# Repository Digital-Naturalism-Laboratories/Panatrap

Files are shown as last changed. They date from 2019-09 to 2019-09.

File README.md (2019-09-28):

# Panatrap
This is an open-source collection of design files and code for turning commercially available 360 "VR" cameras into panoramic camera traps for studying wildlife in natural environments.
These are created in Gamboa, Panama, at Digital Naturalism Laboratories by Andrew Quitmeyer and Danielle Hoogendijk. Work on this project has been supported by:
- The Digital Naturalism Conference (www.dinacon.org)
- Conservation X Labs

## Cameras
The collection currently consists of 2 camera trap setups based on the

- Xiaomi Misphere (MADV in the USA)
 - Full electronic functional control over 
  - Turning camera ON/OFF
  - Switching camera from Video to Photo Mode
  - Trigger a photo or video recording

- Ricoh Theta V
 - Full electronic functional control over
  - Turning the camera on (waking from sleep mode)
  - Triggering a photo or video to begin recording

as we hack more cameras we will add them and their files to this list and repository.
We hacked the Ricoh Theta S and posted detailed instructions here:
but this was quite a destructive hack (we literally ripped the camera apart and soldered things to its button). The Panatrap project focuses on non-destructive, reversible hacks to turn your 360 camera into a cool trap

## Key Challenges
Loosely defined, camera traps are simply photographic instruments that can be remotely triggered by wildlife. Typically this is done with a PIR motion sensor triggering a camera to snap a photo.
Thus when transforming commercially available cameras to become camera traps, the key abilities we need are:
- Remote Triggering
 - The ability to tell the camera to snap a photo or start recording a video
- Low power consumption
 - Typically this is the ability to remotely turn the camera ON/OFF, or at least bring the camera in and out of a low power "sleep mode", and to remotely charge it
- Speedy Capture
 - We were told that a typical camera trap aims to go from sensing an animal's presence to capturing the creature in under 1/2 second
 - This ability is often at odds with the "Low power consumption" goal, since many cameras have a not-insignificant amount of wake up time when starting.
- Image quality
 - An ideal camera trap will provide a high resolution image of the captured animal
- Outdoor Readiness
 - The camera trap needs to be able to withstand being left alone for several days or weeks in its target environment.
 - Camera Traps face challenges from the elements (such as rain, heat, wind, and cold)
 - They also face challenges from local creatures (such as small insect destruction, or elephant smashing)

## Xiaomi Misphere
The first camera that we hacked because it has decent image quality, and importantly it has two exposed electrodes on the camera that make hacking very easy!

They made an interface on the bottom of the camera for the camera to be easily controlled with their included "selfie stick." It's just two metal electrodes that when connected it sends a message to the camera(the original selfie stick has a 220 ohm resistor connected to a button).
From our examinations, the 3 messages you can send to the camera with this interface are:
- Long Press (5 seconds)
 - Camera ON/OFF
- Medium Press (2 seconds)
 - Toggle Recording Mode (Video to Photo, or Photo to Video)
- Short press (0.5-1 seconds)
 - Shutter Button (Take a photo, or start or stop a video)
 
 ### Code
 Code is available in this repo
 
 ### Hardware
 Physical Designs are available here for free download:
 https://a360.co/2nrPLd8
 
 and included in this repo

## Ricoh Theta V
This camera was substantially more locked up  in our attempts to remotely operate it (especially in a way that allows for long term use and have a decently quick trigger).

The camera runs android, and has an acessible USB Api (to recieve PTP commands) and in theory has all the abilities to remotely A) Turn ON/OFF and B)Trigger a Photo Capture. But the firmware blocks some of these features (even if you switch into developer mode).

Luckily we discovered that sending an emulated Keyboard command (through something like a Teensy Arduino 3.2), can remotely wake up the camera (even though this feature is not documented anywhere!), and then we just need to trigger the photo.
The photo triggering is then done by a small servo connected to the arduino which manually taps the shutter button of the camera. The servo is shut down in between photos to reduce power consumption.

 ### Code
 Code is available in this repo
 
 ### Hardware
 Physical Designs are available here for free download:
 https://a360.co/2m22suQ
 and included in this repo

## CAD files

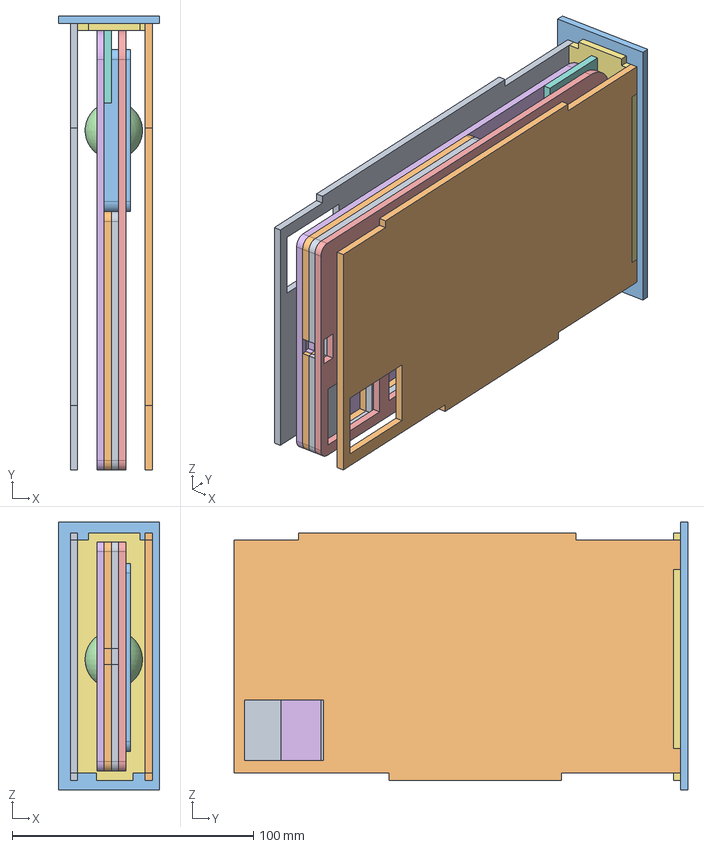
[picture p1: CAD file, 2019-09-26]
MADV/Designs/MADV-weather proof.stp
42.0 x 188.0 x 111.0 mm
holster
MADV body
Top Holder
Back Holder
Weather Sheild

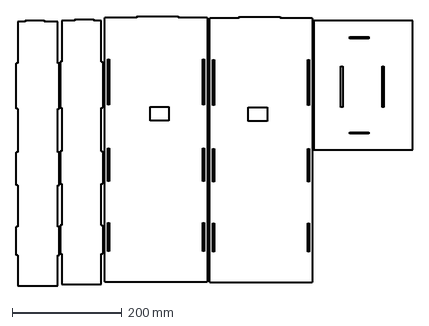
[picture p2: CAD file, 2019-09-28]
Theta_V/Designs/Weather ShieldTheta Servo Trigger Drawing v4 Sheet1.dxf
721.4 x 490.3 mm

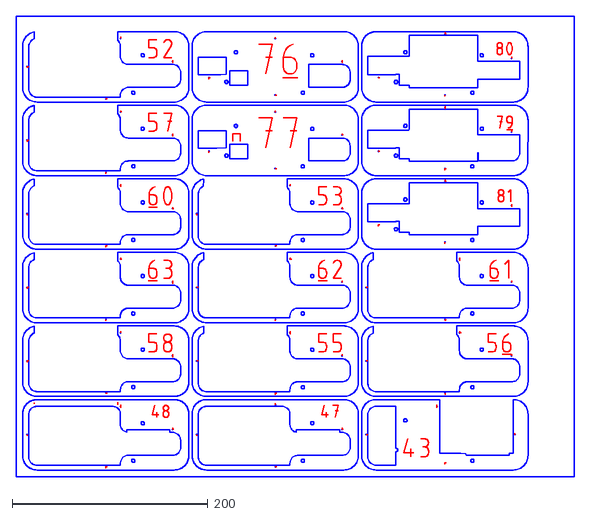
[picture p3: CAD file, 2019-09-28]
Theta_V/Designs/panatrap dxf-0.dxf
570.0 x 470.0

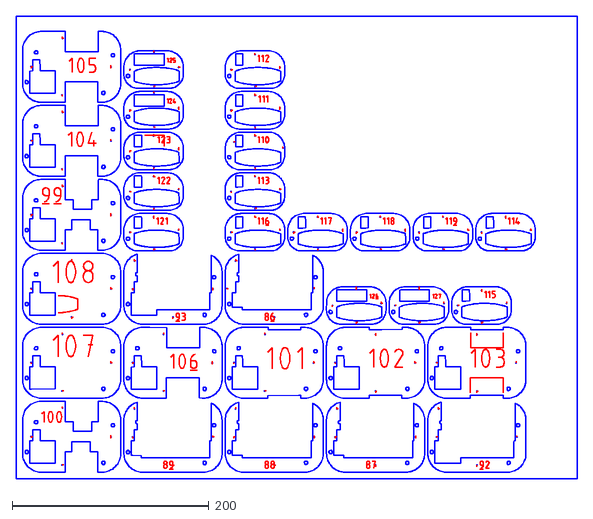
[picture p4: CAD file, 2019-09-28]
Theta_V/Designs/panatrap dxf-5.dxf
570.0 x 470.0

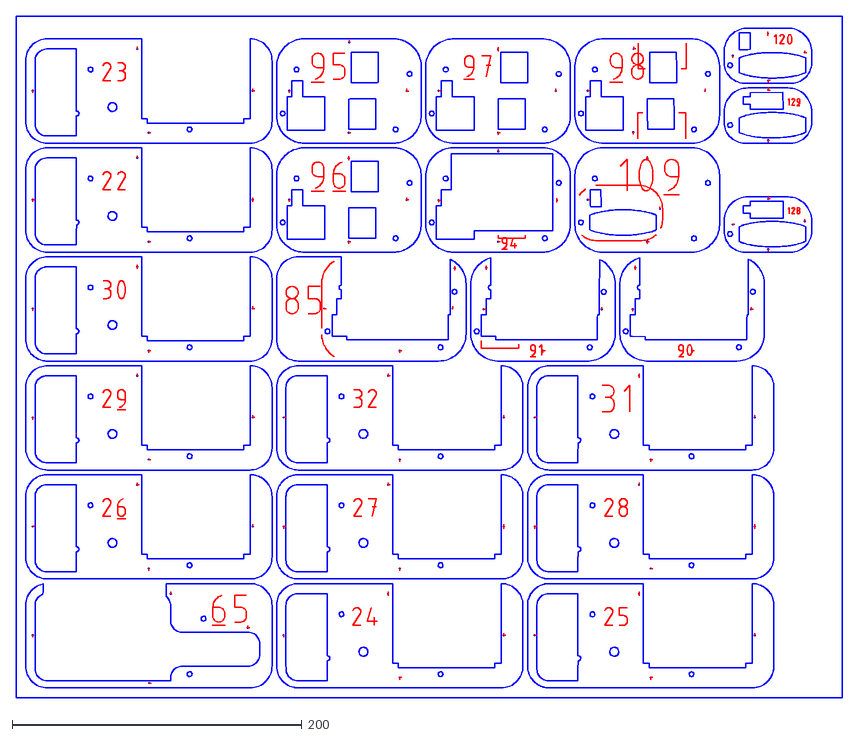
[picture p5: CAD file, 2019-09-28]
Theta_V/Designs/panatrap dxf-4.dxf
570.0 x 470.0

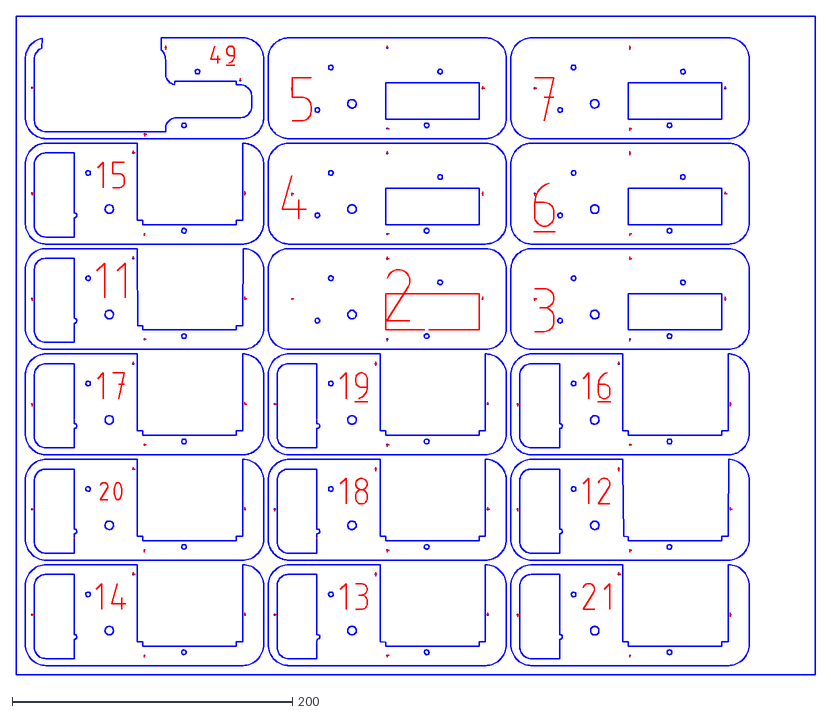
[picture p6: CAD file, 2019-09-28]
Theta_V/Designs/panatrap dxf-2.dxf
570.0 x 470.0

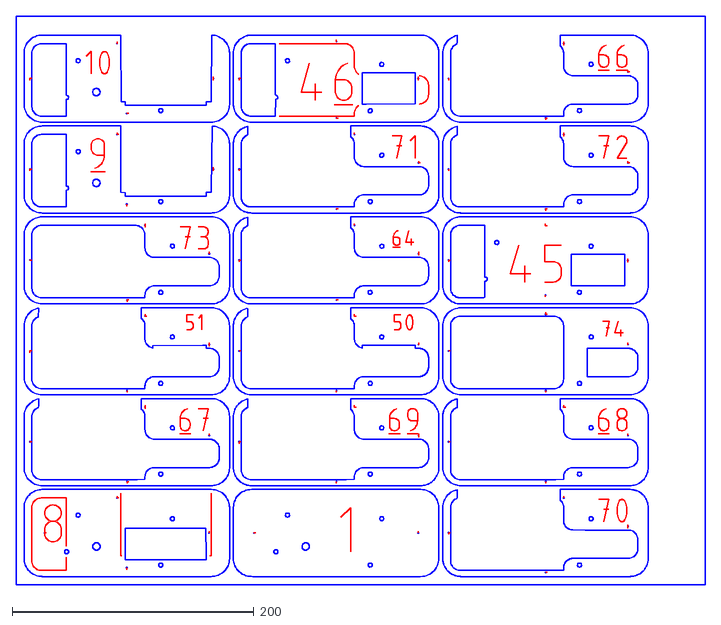
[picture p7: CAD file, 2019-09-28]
Theta_V/Designs/panatrap dxf-3.dxf
570.0 x 470.0

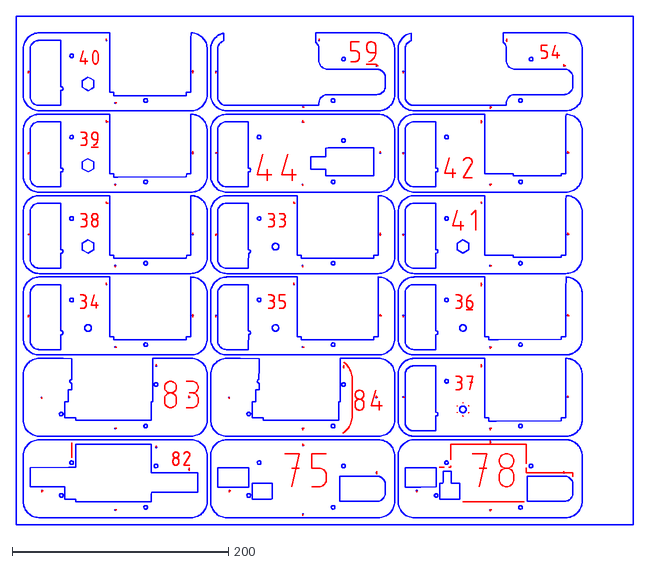
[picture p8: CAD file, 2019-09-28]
Theta_V/Designs/panatrap dxf-1.dxf
570.0 x 470.0

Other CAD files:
MADV/Designs/MADV-weather proof.f3d
MADV/Designs/MADV-weather proof.stl

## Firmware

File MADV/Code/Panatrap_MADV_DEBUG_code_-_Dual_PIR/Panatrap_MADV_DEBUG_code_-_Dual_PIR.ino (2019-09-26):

/*
  PanaTrap - MADV
  Debug Code for the turning the Xiaomi MiSphere (MADV) camera
  into a remotely controlled,
  PIR triggered, Camera Trap

*/

/* in order to trigger the MADV camera to change modes, in theory you should connect a relay to your arduino, and trigger that to connect the nodes of the MADV
  //But we are trying to use minimal hardware, and found that if you connect the node closest to the center of the camera to the ground, and then
  //Connect another digital pin  to the other node
  //Initially set the digital pin to HIGH, and then when you pull it LOW
  //it will trigger the camera

  - Long Press (5 seconds)
  - Camera ON/OFF
  - Medium Press (2 seconds)
  - Toggle Recording Mode (Video to Photo, or Photo to Video)
  - Short press (0.5-1 seconds)
  - Shutter Button (Take a photo, or start or stop a video)

*/

//Front PIR motion sensors
int fPIR = A4;
int fPIRval = -1;

//Back PIR motion sensors
int bPIR = A3;
int bPIRval = -1;

//camera trigger operants

int trigger = 12;
int gndtrigger = 9;


//LED for debugging display
int led = 13;


void setup() {
  //Serial for debugging PIRs
  // initialize serial communication at 9600 bits per second:
  Serial.begin(9600);

  //Turning some of the pins on the camera into virtual Power sources and Grounds
  pinMode(A1, OUTPUT);
  digitalWrite(A1, LOW);

  pinMode(A2, OUTPUT);
  digitalWrite(A2, HIGH);

  pinMode(A5, OUTPUT);
  digitalWrite(A5, LOW);


  //Camera Trigger stuff
  pinMode(led, OUTPUT);
  pinMode(trigger, OUTPUT);
  pinMode(gndtrigger, OUTPUT);

  digitalWrite(led, HIGH);

  digitalWrite(trigger, HIGH);
  digitalWrite(gndtrigger, LOW); //**Andy note A

}

// the loop routine runs over and over again forever:
void loop() {
  // read the input on analog pin 0:
  fPIRval = analogRead(fPIR);
  bPIRval = analogRead(bPIR);
  // print out the value you read:
  Serial.print(fPIRval);
  Serial.print("    rear:  ");
  Serial.println(bPIRval);


  if (fPIRval > 600 || bPIRval > 600) {
    critterDetected();
  }
  delay(1);        // delay in between reads for stability
}

void critterDetected() {

  Serial.println("Critter detected");
  //Turn camera on
  onOffCamera();

  //Take a photo
  takePhoto();
  takePhoto();

  //TODO: Wait to see if other critters still around
  //before we shut off camera

  //TODO: the camera will toggle between photo and video each time it shuts off, add in a toggle here

  onOffCamera();

}

void onOffCamera() {
  Serial.println("cameraONOFF");

  //5 second turn on
  digitalWrite(led, LOW);
  digitalWrite(trigger, LOW);
  digitalWrite(gndtrigger, LOW);
  delay(5000);

  ///Chill
  digitalWrite(led, HIGH);
  digitalWrite(trigger, HIGH);
  digitalWrite(gndtrigger, LOW);
  delay(2000);
}

void takePhoto() {
  Serial.println("Take photo");

  //Take a photo
  digitalWrite(led, LOW);    // turn the LED off by making the voltage LOW
  digitalWrite(trigger, LOW);  // turn the LED on (HIGH is the voltage level)
  digitalWrite(gndtrigger, LOW);
  delay(1000);               // wait for a second

  ///Chill 4 secs
  digitalWrite(led, HIGH);
  digitalWrite(trigger, HIGH);
  digitalWrite(gndtrigger, LOW);
  delay(4000);

}

void togglePhotoVideo() {
  Serial.println("cameraTogglePhotoVideo");

  //2 second press
  digitalWrite(led, LOW);
  digitalWrite(trigger, LOW);
  digitalWrite(gndtrigger, LOW);
  delay(2000);

  ///Chill
  digitalWrite(led, HIGH);
  digitalWrite(trigger, HIGH);
  digitalWrite(gndtrigger, LOW);
  delay(2000);

}

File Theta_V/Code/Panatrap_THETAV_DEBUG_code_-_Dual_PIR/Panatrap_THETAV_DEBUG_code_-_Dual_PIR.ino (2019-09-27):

/*
  PanaTrap - Theta V
  Debug Code for the turning the Ricoh Theta V camera
  into a remotely controlled,
  PIR triggered, Camera Trap

  Using the Teensy 3.2

  This camera is unfortunately blocked in lots of parts of its API from being able to just control with digital signals
    so we control it two ways

    Wake up: Sending a Fake Keyboard Command

    Take Photo:
    Trigger a servo to physically press the button
    Note: if the button is held down WHILE the camera is waking up, it will NOT take a photo, thus there is some timing trickiness here

    Note: make sure to set the Teensy on Serial+Keyboard+Mouse+Joystick

    Note: we are using the Teensy 3.2 because it can send virtual HID signals, and it is the only one I had that was 5V tolerant (which i only had 5V PIRs)
*/

#include <Servo.h>
Servo myservo;
// create servo object to control a servo
// twelve servo objects can be created on most boards

int offpos = 160;
int onpos = 180;


//Front PIR motion sensors
int fPIR = A5;
int fPIRval = -1;
int fPIRpower = 22;
int fPIRgnd = 20;

//Back PIR motion sensors
int bPIR = A2;
int bPIRval = -1;
int bPIRpower = 19;
int bPIRgnd = 17;

//LED for debugging display
int led = 13;

int detectionThreshold = 600; // Our PIRs are actually just binary, but setting up infrastructure in case other sensors are used
void setup() {
  //Serial for debugging PIRs
  // initialize serial communication at 9600 bits per second:
  Serial.begin(9600);
  digitalWrite(led, HIGH);

  //Configure the mouse (im not sure we actually have to do this
  Mouse.screenSize(1920, 1080);  // configure screen size


  //Setup Servo and put it into waiting position
  myservo.attach(23);
  myservo.write(offpos);
  delay(1000); // You have to wait before detaching the servo for it to actually move into position
  myservo.detach();



}


void loop() {

  fPIRval = analogRead(fPIR);
  bPIRval = analogRead(bPIR);
  // print out the value you read
  Serial.print("   Front PIR:  ");
  Serial.print( fPIRval);
  Serial.print("    rear:  ");
  Serial.println(bPIRval);
  Serial.println( analogRead(A3));


  //For the debug code we are just gonna run a simple routine, Field code should have timeouts, and all kinds of other stuff
  if (fPIRval > 600 || bPIRval > 600) {
    critterDetected();
  }

  delay(1);        // delay in between reads for stability
}

//For our Debug code, we are going to just Turn the camera on, and take two photos, or
//conveniently, if we are in Video mode, we will start and stop a video

void critterDetected() {
  Serial.println("Critter detected");
  //Turn camera on
  onOffCamera();

  //Take a photo
  takePhoto();
  takePhoto();

  //TODO: Wait to see if other critters still around
  //before we shut off camera

  //The theta cannot turn off, just turns on
  //It is set to go to sleep after 3 mins, so we just leave it on in case we catch another critter
  //onOffCamera();

}

void onOffCamera() {
  Serial.println("cameraONOFF");
  digitalWrite(led, LOW);

  //Wake the Camera with a Pulse
  Mouse.set_buttons(1, 0, 0);
  myservo.attach(23);
  myservo.write(offpos); // This keeps the camera from just swinging to a random position
  //Wake the Camera with a Pulse

  delay(50); // Wait for a quick click
  Mouse.set_buttons(0, 0, 0);


  //Let camera wake up
  delay(900);

  ///Chill
  digitalWrite(led, HIGH);
}



void takePhoto() {
  Serial.println("Take photo");
    myservo.attach(23);
   myservo.write(onpos);
delay (1200);//hold for like 1.2 seconds

  //Take a photo
  digitalWrite(led, LOW);    // turn the LED off by making the voltage LOW

//Set back to resting mode
    myservo.write(offpos);
   delay(200); //Need a delay or else it detaches before it finish moving
    myservo. detach();


  ///Chill 4 secs // Camera needs 4 seconds to process between photos
  delay(4000);
 digitalWrite(led, HIGH);
}

void togglePhotoVideo() {
  Serial.println("cameraTogglePhotoVideo");

  //2 second press
  digitalWrite(led, LOW);

  delay(2000);

  ///Chill
  digitalWrite(led, HIGH);

  delay(2000);

}

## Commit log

2019-09-26 Added Design Files and updated code
    [MADV-weather proof.f3d, MADV-weather proof.stl, MADV-weather proof.stp]
2019-09-26 Create Theta Servo Trigger.f3z
2019-09-27 Added Sliced Files of latest version
    [panatrap2 dxf-0.dxf, panatrap2 dxf-1.dxf, panatrap2 dxf-2.dxf, panatrap2 dxf-3.dxf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]
2019-09-27 Fixed hole
    [panatrap2 dxf-0.dxf, panatrap2 dxf-1.dxf, panatrap2 dxf-2.dxf, panatrap2 dxf-3.dxf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]
2019-09-28 Updated Design Files to latest version
    [Weather ShieldTheta Servo Trigger Drawing v4 Sheet1.dxf, panatrap dxf-0.dxf, panatrap dxf-1.dxf, panatrap dxf-2.dxf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]
